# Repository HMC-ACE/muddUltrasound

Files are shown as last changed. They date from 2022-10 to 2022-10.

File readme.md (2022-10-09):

Low-Cost Underwater Ultrasonic Phased Array Research Platform
-------------------------------------------------------------

This repo contains all PCB designs, SAM4s MCU firmware, python imaging code, and documentation for the phased array research platform.

For full documentation, see [link](doc/build/html/index.html) (in a browser, you'll need to clone the repo first).

Directory
--------
 - `doc` contains the documentation source and build files (using sphinx).
 - `pcb` contains the KiCad PCB files for the channel boards and center board.
 - `mcu` contains the Atmel Studio project files for the MCU firmware.
 - `scripts` contains all python scripts to be run on the host computer.

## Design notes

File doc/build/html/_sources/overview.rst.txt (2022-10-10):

========
Overview
========

Describe assembly connection: Transducer array -> motherboard -> 9 channel boards -> i2c bus controlled by FTDI breakout -> control computer
Describe equipment connections: Hook power supplies to channel boards and motherboard by daisy chaining or w/e (star network), it will distribute power
Describe flashing boards – Atmel compiler, something something, not full depth
Describe running software on host computer – sends commands from Python over USB
Describe other subsections – one per board, maybe top level scripts

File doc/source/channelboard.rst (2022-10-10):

.. _ref-channelboard:

=============
Channel Board
=============

Outline
-------

This section contains information on the channel boards including their operation, features, configuration options, and connections. This section contains the KiCAD PCB files as well as Gerber fabrication outputs for manufacturing these boards. The Bill-of-Materials spreadsheet is also included.

File Structure
--------------

.. code:: text

  - pcb/
    - channel-board/
      - BOM.xlsx             <- Bill of Materials
      - BoatCentralboard.pro <- main KiCad 5 project file 
      - BoatCentralBoard.*   <- misc KiCad 5 project files
      - fp-lib-table         <- KiCad project footprint library location table
      - sym-lib-table        <- KiCad project symbol library location table
      - Fabrication Files/   <- GERBER files for fabrication

Board Overview
--------------

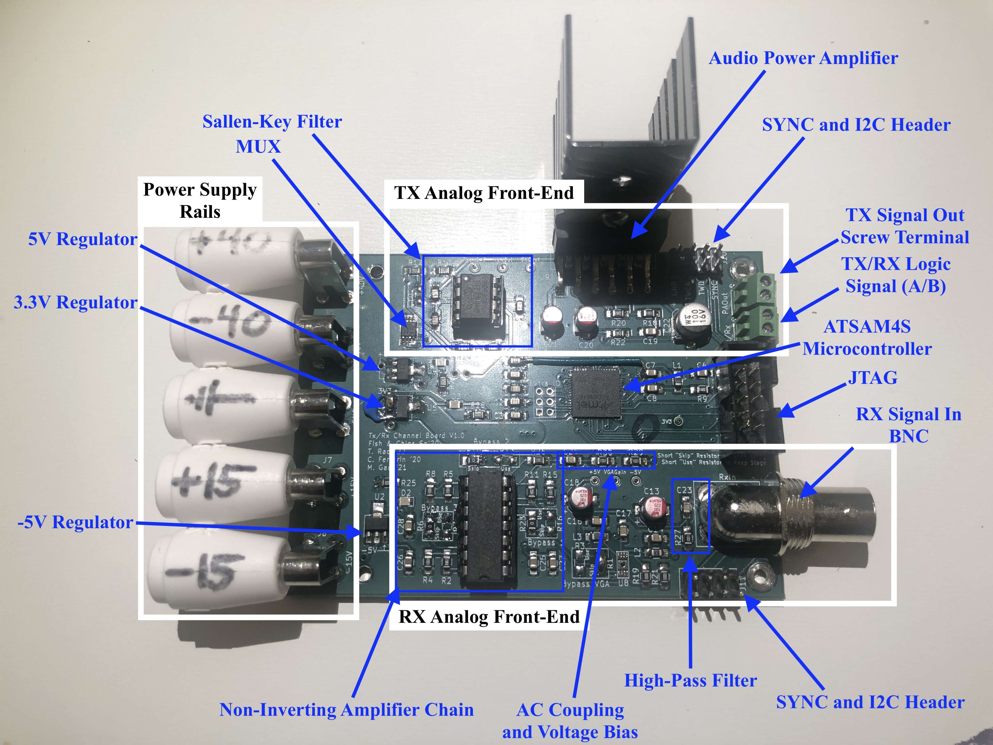
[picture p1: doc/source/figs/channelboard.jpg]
Picture of the channelboard calling out features


Each channel board is capable of driving both the transmit (TX) and receive (RX) operations for a single piezoelectric transducer in the array. An ATSAM4S microcontroller is used for PWM generation, ADC sampling, DAC output, I2C communications, and other functions. The board contains both a TX and RX analog front-end. The TX front end generates a high-voltage sinusoidal pulse to drive the transducers. This signal is output to the central motherboard with a screw terminal connector. The RX front end accepts an incoming signal from the motherboard with a BNC connector, then filters and amplifies the signal before it is sampled.  The board requires five voltage rails, typically supplied by benchtop power supplies over banana cables: ±40V, ±15V and ground. It also contains two headers at the top and bottom for the I2C and SYNC signals, so multiple channel boards can be linked on the same bus by ribbon cables. Other connectors include a JTAG programming header for the microcontroller and a screw terminal for the TX/RX switch logic signal. Due to the modular design, the entire array can be easily scaled up from the 3x3 array used in our work.

Picture of the channelboard layout for the 3x3 array

The nine-channel layout with the central board is shown in the above image. Note that not all connections between boards are shown.

Theory of Operation
-------------------

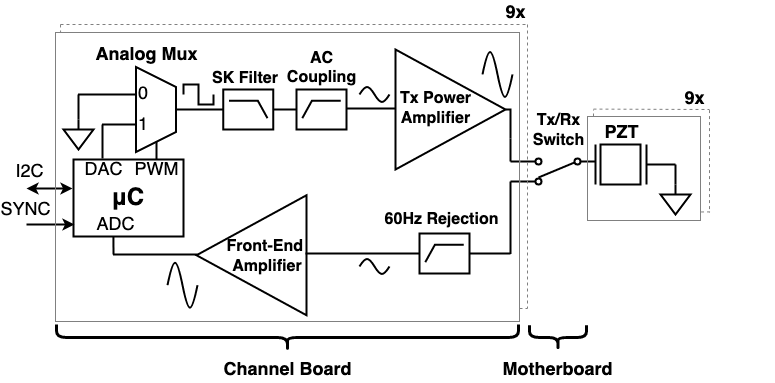
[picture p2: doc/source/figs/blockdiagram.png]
Block Diagram of the Channel Board


The channel circuitry is made of two analog front ends: a TX AFE that drives the piezoelectric transducer, and an RX AFE that amplifies and filters signals reflected back to the transducers. The image above shows a block diagram of both front-ends.

The TX AFE creates a high-voltage sinusoidal burst. The TX AFE can generate bursts with adjustable initial delays, burst amplitudes, and burst durations. When initiated by the rising edge of a digital signal called SYNC, the timer peripheral in each channel's microcontroller waits for an initial delay, then it generates a 92kHz pulse-width modulated (PWM)  signal, typically with a 100us duration. The PWM burst drives the select line of an analog multiplexer, which causes the output of the multiplexer to switch between ground and a digital-to-analog converter (DAC) voltage.  The DAC voltage is also generated by the microcontroller. The multiplexer output is driven into a set of amplifiers and filters, and because the amplifiers and filters have a fixed gain, the transmitted signal's amplitude is controlled by the DAC voltage.

One of the circuits in the TX AFE signal chain is a Sallen-Key low pass filter that is used to filter harmonics out of the multiplexer output.  Removing these harmonics converts the output from a square wave to a sine wave.  The output of the Sallen-Key filter is AC-coupled into a linear audio amplifier (the LM3886T), which amplifiers the signal to a maximum voltage swing of ±40V. The output of the amplifier is connected to a TX/RX switch (located on the central board), which in turn is connected to the piezoelectric transducers.

The RX AFE on each channel amplifies the signal with a high gain, then samples the signal coherently with the other channels. The first stage of the RX front-end is a first-order high-pass filter used for AC coupling and 60Hz rejection. The remaining stages comprise a multi-stage op-amp-based
amplifier. The final stage of the voltage amplifier drives a series current limiting resistor, AC coupling capacitor, and voltage divider used to bias the signal to a 0-3.3V range. The RX AFE output is sampled at 1 MSPS by a 12-bit ADC (with 10.5 effective bits) embedded in the channel microcontroller. Each channel's ADC used the same 1MHz clock in order to synchronize the samples. Sampling is triggered by the falling edge of the SYNC signal. Data is stored in RAM via DMA transfer and is offloaded back to the host computer for processing after sampling is complete.

Configuration Options
---------------------

The channel board offers a few options to reconfigure the TX and RX analog front-ends.

The TX Sallen-Key filter is designed to have a corner frequency near the resonant frequency of our specific transducers, which is 92kHz. The resistor and capacitor values of this filter can be changed depending on the resonant frequency of your transducers.

The RX 1st-order RC high-pass filter (R27 and C23) is tuned to reject 60Hz mains pass-through that was in our testing environment. This can be tuned to your needs, as well.

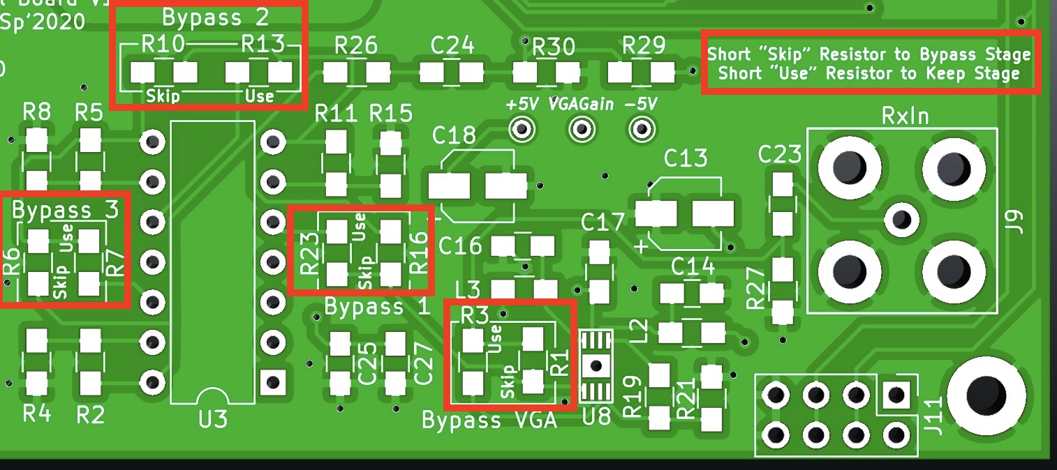
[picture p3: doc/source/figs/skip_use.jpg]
A figure showing the set of 0 ohm resistor population options


The RX amplifier chain has several 0Ω resistor population options that can change the final gain of the RX signal, as seen in the above image. There are three non-inverting amplifiers, each with a gain of approximately 20.8dB. For our tests, a gain of 41.6 dB is used (two amplifier stages are used, one is skipped).

There is a population option for an AD8337 Variable Gain Amplifier (VGA) on these boards. The gain control voltage is provided by the second DAC channel on the microcontroller. This component was not populated for our tests, and we recommend that this component not be populated if unused.

The board includes test points for the signal at each stage of the TX chain. There are also test points for all voltage rails. Indication LEDs also display whether a voltage rail is on or not.

Power Connections
-----------------

The five voltage rails — ±40V, ±15V and ground — can be supplied via banana cables from benchtop power supplies. The ±15V rail is used to generate 5V and 3.3V rails, and the -15V rail is used to generate the -5V rail on the board. The ±40V rails are used for the TX audio power amplifier.

Clock Distribution
------------------

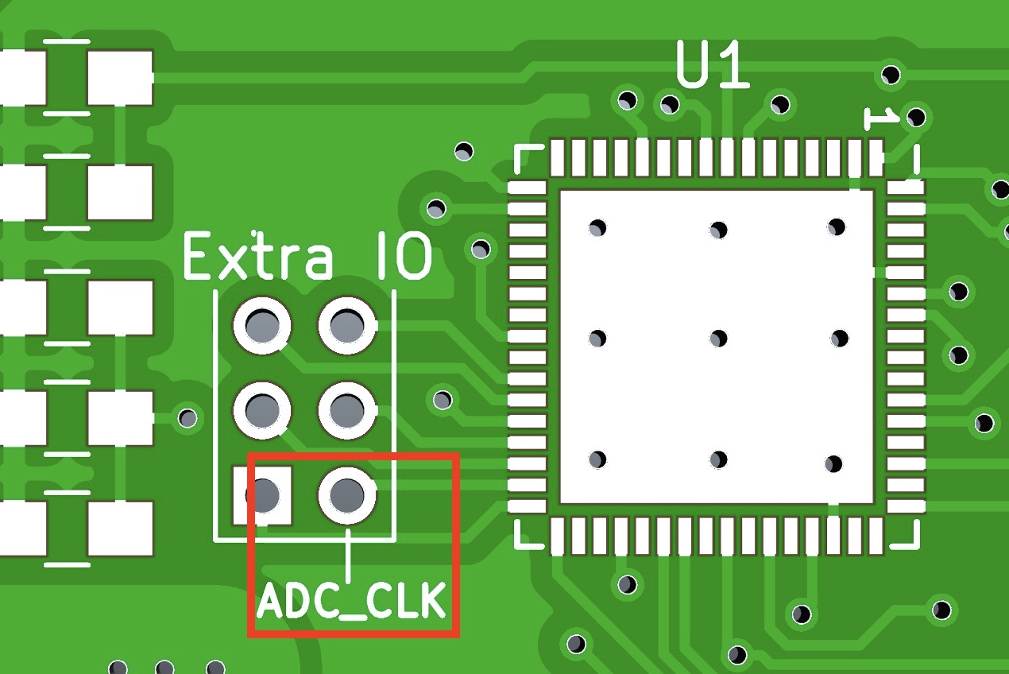
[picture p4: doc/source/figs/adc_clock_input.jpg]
Figure showing the sample clock input pin


A shared 1MHz clock must be distributed to each channel board by soldering wires to the appropriate through-hole connection on the channel board. This signal is used to generate each channel’s ADC sampling clock. The shared clock bus ensures that each channel has a synchronized sample period.

Programming Guide
-----------------

To program the channel microcontrollers the 15V rail must be provided so that the microcontrollers receive 3.3V. Plug in the JTAG connector from your programming device to the board with the correct orientation. Further instructions can be found in :ref:`ref-flashingboards`.

-- Tejus Rao

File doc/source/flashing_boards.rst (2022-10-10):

.. _ref-flashingboards:

===============
Flashing Boards
===============

The SAM4S microcontrollers onboard the channel boards were programmed using `Microchip studio`_.

Open the ``.atsln`` ("atmel solution") project file to get started. When flashing the microcontrollers, only the +15V rail needs to be powered. Open the "Programming Dialog" (`Programming Dialog Documentation`_) to flash the boards with the firmware. We use the `Jlink EDU mini`_ programmer. Go `tools > device programming` to select the options for this. Make sure that everything is wired right and connected by reading the voltage of the bus, and it should be 3.3v. Then you can try reading the device ID.

Note that you need to set the specific flavor of SAM4s MCU that you are using before you can program it, because it checks the device ID.  Our array uses the ``SAM4S4B`` and ``SAM4SA16B`` flavors, and we expect that you'll use drop-in replacements depending on part availability.

.. note::
   When programming each channel boards, the i2c address in the source code needs to be set to correspond to that of whichever board is being programmed (in line 33 of ``main.c``). A simple way to check that all boards have the correct addresses is to run ``python -i i2c_cmd.py``. If there are not 9 boards with unique addresses 1-9, the instantiation of the PhasedArray object will fail up when addressing the channel boards to write DAC values.

File Structure
--------------

.. code:: text

   - mcu/
     - rcvchain_asf_devel.atsln   <- the project file for Microchip Studio
     - rcvchain_asf_devel/
       - src/
         - main.c                 <- the main code
         - main.h                 <- the main header file
         - asf.h                  <- autogenerated include file for Atmel Software Framework
         - config/
           - config_clock.h       <- the clock configuration defines
           - config_board.h       <- unused
         - lib/
           - crc.c                <- cyclic redundancy check (crc) implementation
           - crc.h                <- crc implementation header file
        - ASF/                    <- Atmel Software Framework

Notes on the Code
-----------------

The primary purpose of the MCU firmware is to set initialize a peripherals that enable the transmit and receive functionality of each channel.
 - The I2C interface is brought up as the main method of communication with the host PC. During normal operation, when performing a write operation, the host PC either sets DAC values and transmit phase shift values. The host has other options as well, such as manually turning on and off the PWM, for debugging purposes. When performing a read operation, the host reads the channel buffer (e.g. the signal recorded by ADC). See ``TWI0_Handler`` in ``main.c`` for more information.
 - The ADC is also configured to sample from an external clock and output data to a sample buffer (``frame_buffer``) using the Peripheral DMA Controller (PDC) peripheral.
 - The PWM peripheral is set up for a 92 KHz square wave.
 - A DACC channel is used to set the amplitude of the square wave exiting from the analog multiplexer.
 - A GPIO interrupt handler ``PIOA`` is setup to start transmit on the rising edge of a sync pulse, and start receive on the falling edge.

The source code, for the most part, sticks to using the `"Advanced Software Framework"`_ (ASF), which is a Hardware Abstraction Layer (HAL) that should, theoretically, ease development. The `SAM4s datasheet`_ has good documentation of the SAM4s, and the ASF_ is documented as well. In practice, it is also helpful to use the "go to definition" feature in Microchip Studio to open the ASF file where the ASF functions are implemented.

The  ASF is bypassed in the case of the ``PIOA`` interrupt handler because the ASF-provided interrupt handler has extraneous logic that affects the execution time of the handler. The interrupt vector table (table containing all of the addresses to interrupt handlers) is replaced in order to bypass this. See comments in the ``src/main.c`` file itself for info. This file contains everything except for the clock configuration, which can be found in ``src/config/conf_clock.h``, and the crc calculation code taken from the internet (in public domain), which can be found in ``lib/crc.h``

If the user desires to expand the capabilities of the firmware, the "ASF Wizard" can be used to load the specific module for the peripheral of interest.

.. _`Microchip studio`: https://www.microchip.com/en-us/development-tools-tools-and-software/microchip-studio-for-avr-and-sam-devices#tabs
.. _`"Advanced Software Framework"`: https://asf.microchip.com/docs/latest/search.html?device=sam4s
.. _`Programming Dialog Documentation`: https://onlinedocs.microchip.com/pr/GUID-ECD8A826-B1DA-44FC-BE0B-5A53418A47BD-en-US-12/index.html?GUID-56262FE6-0BB6-49BF-974C-884E279F0A57
.. _`SAM4s datasheet`: https://ww1.microchip.com/downloads/en/DeviceDoc/Atmel-11100-32-bit%20Cortex-M4-Microcontroller-SAM4S_Datasheet.pdf
.. _ASF: https://asf.microchip.com/docs/latest/search.html?device=sam4s
.. _`Jlink EDU mini`: https://www.segger.com/products/debug-probes/j-link/models/j-link-edu-mini/

-- Alec Vercruysse

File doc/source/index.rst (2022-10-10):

.. fish-n-chips-array documentation master file, created by
   sphinx-quickstart on Tue Jul 20 15:23:22 2021.
   You can adapt this file completely to your liking, but it should at least
   contain the root `toctree` directive.

Ultrasonic Phased Array Research Platform Documentation
=======================================================

This is the main page for the documentation of the phased array research platform.

The :ref:`ref-array` page provides an overview of the assembly of the piezoelectric elements.
The :ref:`ref-motherboard` page describes the assembly and wiring of the central board.
The :ref:`ref-channelboard` page describes the assembly and wiring of the channel boards.
The :ref:`ref-flashingboards` page describes how to program the microcontrollers on each channel board.
The :ref:`ref-software` page describes how to connect to the array with the PC and run imaging scripts. It also includes the :ref:`ref-api`.

.. toctree::
   :maxdepth: 2
   :caption: Contents:

   transducer
   motherboard
   channelboard
   flashing_boards
   running_software
   usage

Indices and tables
==================

* :ref:`genindex`
* :ref:`modindex`
* :ref:`search`

Building this Documentation
---------------------------

This documentation is built with sphinx. To rebuild the documentation, first ensure that you have a virtual environment with all the required modules for the python scripts. The virtual environment also needs ``sphinx`` and ``sphinx_rtd_theme``. In a terminal with the ``doc`` folder as the working directory, run ``make clean; make html`` to build. All files should appear in ``doc/build``.

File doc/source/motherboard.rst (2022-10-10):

.. _ref-motherboard:

===========
Motherboard
===========

This section contains information about the central board, or motherboard, used to route TX signals to and RX signals from the transducer array. This section contains the KiCAD PCB files as well as Gerber fabrication outputs for manufacturing these boards. The Bill-of-Materials spreadsheet is also included.

File Structure
--------------

.. code:: text

  - pcb/
    - center-board/
      - BOM.xlsx             <- Bill of Materials
      - BoatCentralboard.pro <- main KiCad 5 project file 
      - BoatCentralBoard.*   <- misc KiCad 5 project files
      - fp-lib-table         <- KiCad project footprint library location table
      - sym-lib-table        <- KiCad project symbol library location table
      - Fabrication Files/   <- GERBER files for fabrication

Board Overview
--------------

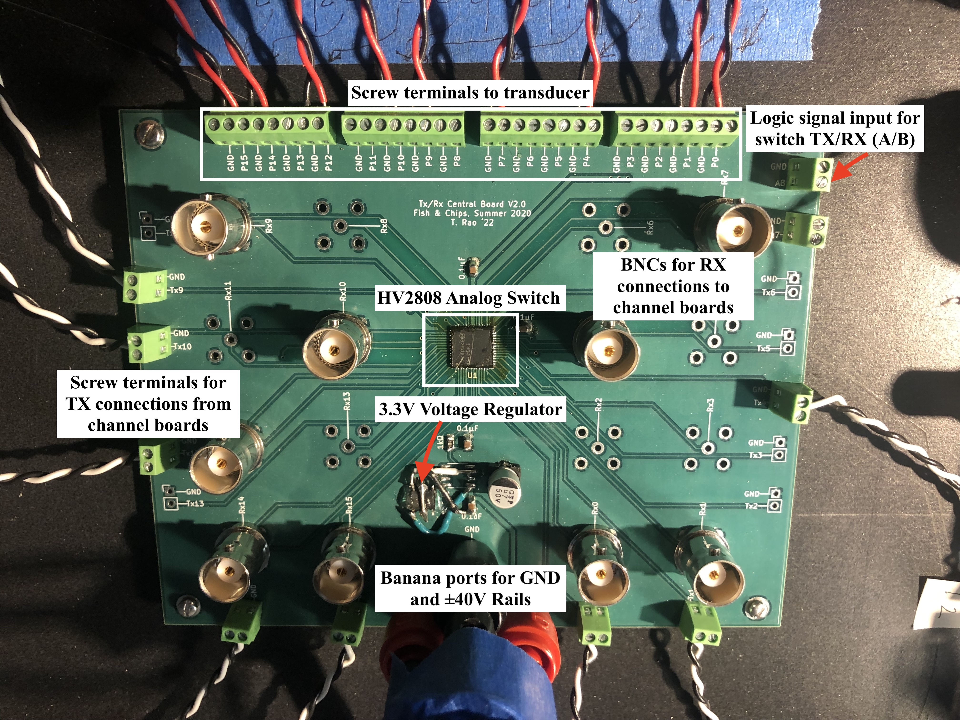
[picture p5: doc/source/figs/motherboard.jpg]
Picture of the motherboard calling out features


  Picture of the Motherboard
          
The central board hosts a Microchip HV2808 32-channel high-voltage analog switch. This device acts as a TX / RX switch to isolate the TX and RX analog front ends during their respective operations. This board breaks out the HV2808 into 32 ports, enabling a 16 channel TX / RX switch. The other components on this board are a 3.3V voltage regulator and power supply decoupling.

.. note::
   Note that the board pictured does not have all components soldered. Only connections for channels 0 through 8 were populated since this was used for a 9 channel (3x3) transducer array.

.. note::
   Note that the rework visible on the board pictured was due to an incorrect voltage regulator footprint, which has since been updated in the PCB files.

Connections
-----------

The RX connections use vertical-launch female BNC ports to improve signal integrity, while the TX connections use side-launch screw terminals. Connections between the TX screw terminals on the channel boards and this central board were made with twisted pairs of 22 AWG solid-core wire. Other connectors include the screw terminal bank for connecting to the piezoelectric transducer array and banana ports for positive and negative 40V rails, and ground. The ±40V and ground rails should be linked to the same power rails as the channel board. Additionally, the screw terminal labeled “A/B” is the logic input for switching the HV2808 conduction path. It’s compatible with a 3.3V signal from the channel microcontrollers.

All channel boards contain connections to output the A/B switching signal to the central board, but only one must be connected. This is nominally channel 0. Connection between the channel 0 board and central board A/B terminal is done over a twisted pair of 22 AWG solid-core wire.

Soldering Instructions
----------------------

If using solder paste with or without a stencil, we recommend soldering the surface-mount components before the larger through-hole connectors. Ensure connections on the QFN-package HV2808 are not shorted. Perform rework as necessary before proceeding to soldering the through-hole components.

-- Tejus Rao

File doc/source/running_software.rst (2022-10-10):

================
Running Software
================

We communicate with the nine channel boards with a host PC and a FTDI FT2232H-56Q evaluation board, which contains an FTDI FT2232H USB to I2C device. All python software is written to run on the host PC.

This API documentation provides the docstrings for the methods used to interact with the Phased Array through the FT2232H chip. All PC to board and board to PC communication is done with methods in the `i2c_cmd` module. Also documented here is `das_scan`, which is the module that contains all of the different imaging scripts, and `visualize`, which is the module that allows "replay" of the imaging done in `das_scan`.

All of these modules are located in the ``scripts/`` directory, and can be run themselves (not just imported).

.. _ref-software:

Communicating with the Array
----------------------------

Wiring
~~~~~~

See below for i2c wiring (also documented in pyftdi_)

.. _pyftdi: https://eblot.github.io/pyftdi/api/i2c.html#wiring
.. _`pyftdi documentation`: https://eblot.github.io/pyftdi/api/i2c.html#open-collector-bus 

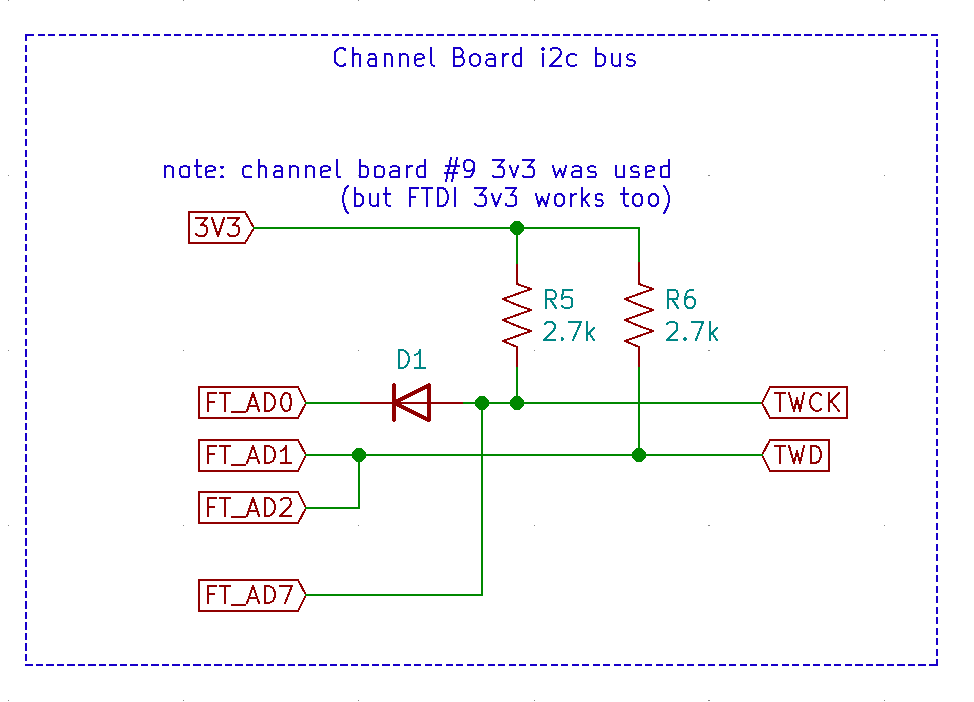
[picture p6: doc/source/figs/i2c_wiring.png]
I2C wiring


  Fig.1: FT2232H i2c wiring. note the `FT_` prefix won't appear on the silkscreen of the `FT2232H-56Q` itself.

The SYNC pulse is also generated by the GPIO of the `FT2232H`, and is used by all boards to start a TX operation at the exact same time, and an RX operation at the exact same time. This extremely important to the operation of the phased array since any time difference between the start of the TX or RX operations for different boards will cause destructive phase differences during beamforming. The internal oscillators in the microcontrollers have some frequency offset relative to each other, so the FT2232H provides a SYNC pulse to trigger both the start of the TX and start of the RX operations. The rising edge of the SYNC pulse controls the start of the TX operation, and the falling edge controls the start of the RX operation. We need to have a deterministic and precise amount of time between the start of a TX and the start of an RX, since this delay has to be taken into account when range-finding. Furthermore, we want to be able vary the amount of time between the start of a TX and the start of an RX sequence, since having some delay between the end of the TX and the start of the RX allows the piezos to stop "ringing" before receiving the echo signals. This affects the minimum range that the phased array can image. The FT2232H cannot provide the deterministic timing for the SYNC pulse because it is controlled via USB by a non real time operating system (e.g. the host computer), so the pulse width is non-deterministic. We solve this by using a 555 timer in a `monostable configuration`_, with a trim potentiometer to allow us to vary the pulse width. The 555 timer is triggered by a GPIO output of the FT2232H. In our implementation, the 556 timer was tuned to a 800 us delay. If this is changed, ``PhasedArray.delay`` should be set to what it is tuned to in ``i2c_cmd.py``.

.. _`monostable configuration`: https://www.electronics-tutorials.ws/waveforms/555_timer.html

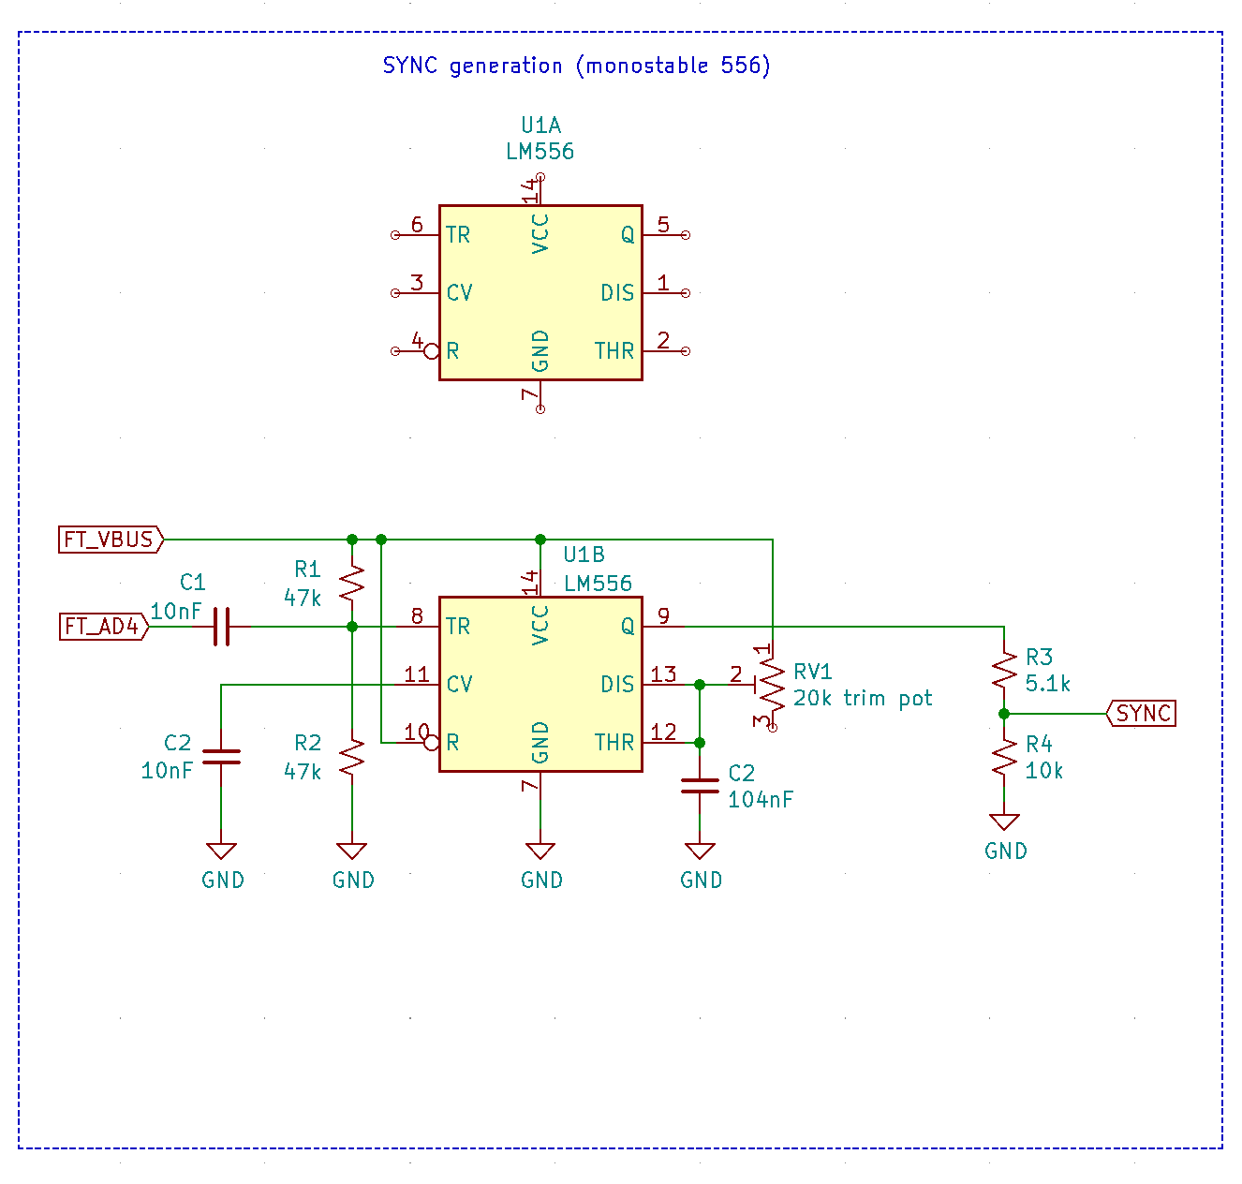
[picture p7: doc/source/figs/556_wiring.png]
555/556 wiring for SYNC pulse generation.


  Fig.2: 555/556 wiring for SYNC pulse generation.

The wiring schematic file can be found in ``./figs/fish-n-chips-ft2232h``.

Software Setup
~~~~~~~~~~~~~~

To run the python code, first set up a virtual environment using the provided ``requirements.txt``. Note that ``pyfti`` is used to interface with the FTDI FT2232H-56Q evaluation board.

Ensure the FTDI chip is connected via USB to the host PC. Running ``python -i i2c_cmd.py`` will start python in interactive mode, and `i2c_cmd` will create a `PhasedArray` and `ChannelBoard` object for the user to interact with. Running this is the simplest way to check that the host PC is able to communicate with each channel board.

Once the `ChannelBoard` object is instantiated, `i2c_cmd` facilitates simple analog front-end (AFE) debugging. For example, ``ChannelBoard.write(BoardApi.START_PWM)`` will indefinitely turn on the PWM for the instantiated channel board. In the REPL, see ``help(PhasedArray)``, ``help(ChannelBoard)``, and ``help(BoardAPI)`` for more options.

To facilitate debugging the receive analog front end, `read_frambuffer.py` enables simple visualization of samples recorded by the ADC of a channel board. Run ``python3 read_framebuffer.py -h`` for usage information.

.. note:: The i2c read/writes fail occasionally, and we make sure to allow for many re-tries when things go wrong, as well as check the integrity of read data with a crc32 checksum. If an i2c or checksum error occurs, it usually resolves within 10 tries, but very rarely takes longer.

.. _ref-imaging:

Imaging
-------

All the code for the different types of swept-beam imaging is housed in ``das_scan.py``. Note that each type of imaging takes a very long time -- points are scanned in a 2D or 3D space by sending a steered transmit pulse and performing beamforming on the receive. The time taken to perform each set of transmit/receive is limited mostly by the slow speed of the i2c communication.

Running `das_scan.py` as main will run a spherical imaging script. Note that there will be a prompt for the "setup:", which is simply a note the user can write in order to name or comment on the specific image run being taken, for when the captured data is later analyzed.

Logging is enabled by default into a directory called `data/` (relative to the `scripts/` directory). Running `visualize.py`  allows the user to interactively select and view an imaging run to inspect and review.

To run a 2D scan, try running the ``scan_x_slice`` function that `das_scan` provides. There is no raw data logging option for this yet.

File Structure
--------------

.. code:: text

          - scripts/
            - das_scan.py         <- The top-level code for swept-beam imaging.
            - i2c_cmd.py          <- The code containing the interface to each channel board.
            - image.py            <- The code to perform delay-sum beamforming.
            - phaseshifts.py      <- The code to calculate phase shifts for steering directions.
            - read_framebuffer.py <- Debug code to visualize the output of an ADC capture.
            - requirements.txt    <- Used to set up a virtual environment with the necessary python packages.
            - visualize.py        <- Used to visualize (e.g. replay) logged data from das_scan.

.. _ref-api:
              
API Documentation
-----------------

.. toctree::
   :maxdepth: 2
   :caption: Contents:

   api/i2c_cmd
   api/das_scan
   api/visualize

-- Alec Vercruysse

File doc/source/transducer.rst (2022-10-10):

.. _ref-array:

================
Transducer Array
================

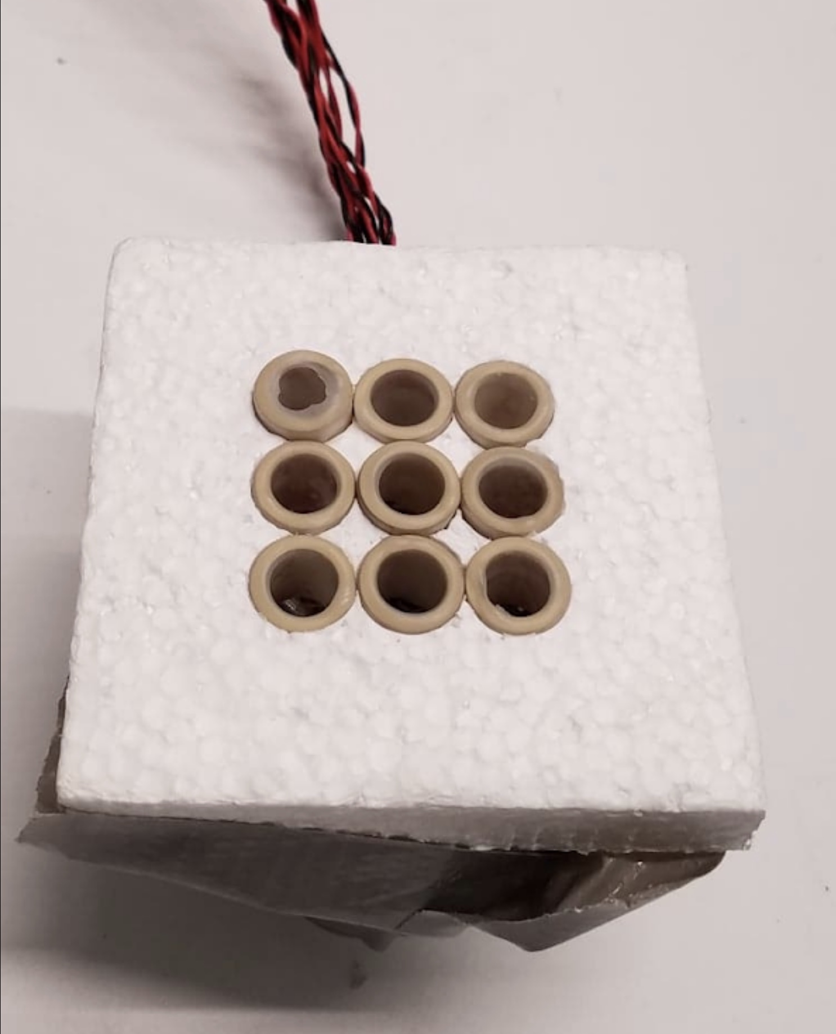
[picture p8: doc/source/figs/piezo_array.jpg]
Image of pzt array.


Outline
-------

This section contains information on the piezoelectric transducer array, the process for coating each transducer with silicone, and guidelines for creating the array assembly. The transducers used are the `American Piezo (APC) 42-1012`_ (may be available as the 42-1011, as well) cylindrical tube.

Soldering to the transducers
----------------------------

The piezoelectric cylinders are plated with a very delicate layer of metal, which enables us to solder connections to them. Take care to follow the instructions outlined by American Piezo when soldering connections to them. We recommend purchasing the American Piezo `soldering kit`_ to practice soldering to piezo samples. It’s critical to use low-temperature solder and flux, and to minimize the duration of direct heat in contact with the transducers in order to preserve the metal plating on the transducer and prevent the ceramic from cracking.

The outer ring of the cylinder is considered to be ground.

The procedure that we used is outlined here:

*Materials (per transducer)*
 - APC 42-1012 piezo
 - 5ft of 22 AWG solid-core wire (twisted pairs, usually red and black or white and black)
 - Flux paste
 - Low-temperature rosin-core solder
 - Soldering iron
 - Flux remover spray or IPA
 - Kapton or masking tape

*Instructions*
 1. Secure the piezo cylinder with tape to your work surface
 2. Strip about 5mm of insulation off both ends of the wires
 3. Apply a layer of solder to the exposed wires (aka tinning)
 4. Coat the exposed wire with flux paste. Rosin flux paste will also help the wire adhere to the surface of the piezo before soldering since it is slightly sticky.
 5. Mount or hold your wires to the transducer with the ground wire on the outer surface and the signal wire on the inner surface of the cylinder.
 6. Melt a bead of solder onto the soldering iron tip
 7. Carefully press the melted solder on the tip to the exposed wires on the piezo ring. When the solder has flowed and created a connection, remove the iron. The joint should be flat and shiny.
 8. Remove excess flux
 
Coating Process
---------------

The ceramic transducers have an acoustic impedance that is quite different from that of water. We coat the transducers with a thin layer of silicone, which has an acoustic impedance much closer to that of water, to increase our power transfer into the water. The coating we used is the `Silicone Solutions SS-6B`_.

This process should be completed after soldering wires to the piezos. Note that the process can be messy, so prepare a surface for the excess silicone to drip onto beforehand. We recommend hanging the transducers by their wires over an open area with tape and using paper towels to protect the surface below. We space the transducers a couple inches apart.

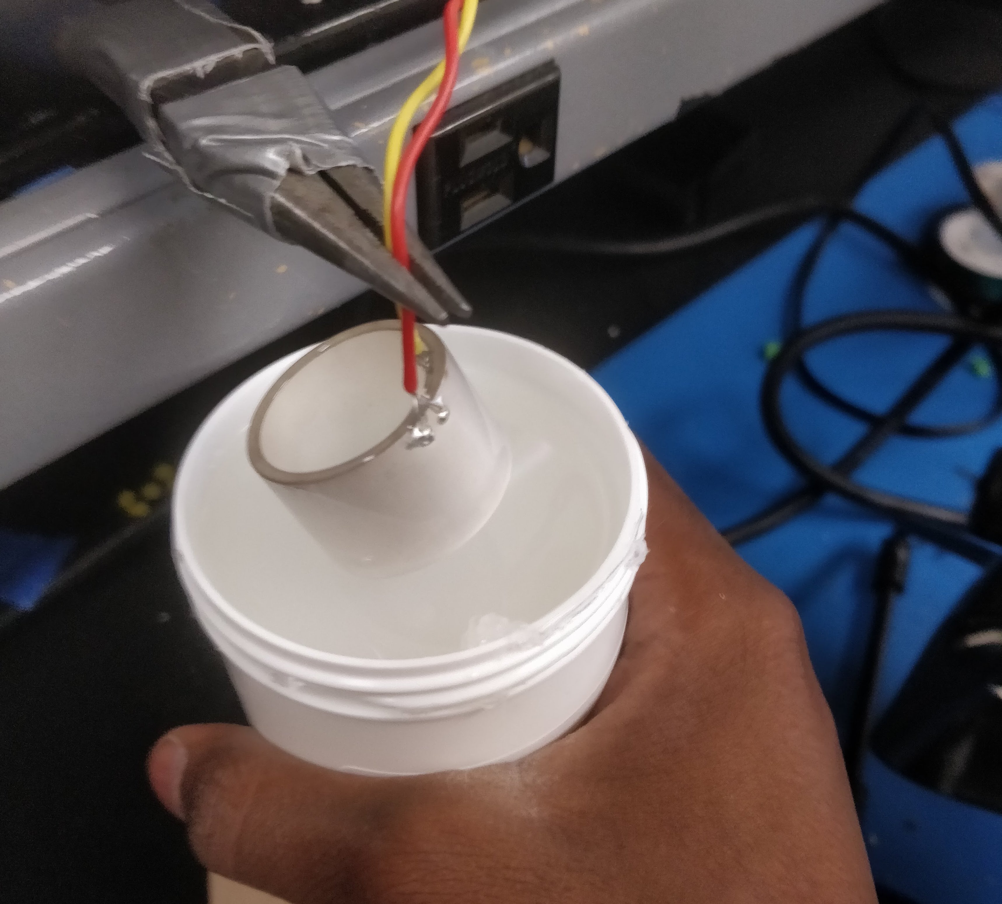
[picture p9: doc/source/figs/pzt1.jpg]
Inserting the tub of coating around the pzt.


Without moving the piezo, insert the tub of coating around each. Ensure that the entire piezo is coated, along with any exposed wire.

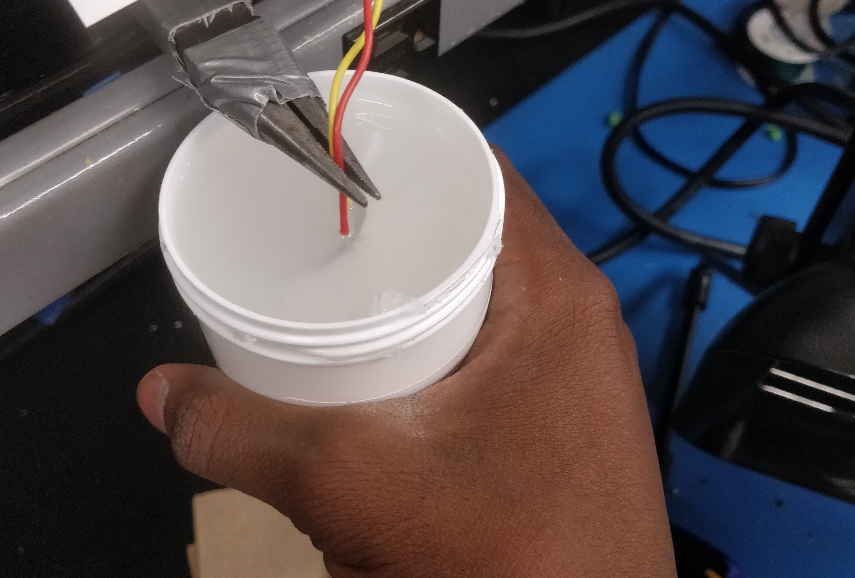
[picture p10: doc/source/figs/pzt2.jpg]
Second image, inserting the tub of coating around the pzt.


Slowly remove the tub from the cylinder and repeat on every piezo. Let the coating dry in a well-ventilated area for the manufacturer’s recommended cure time.

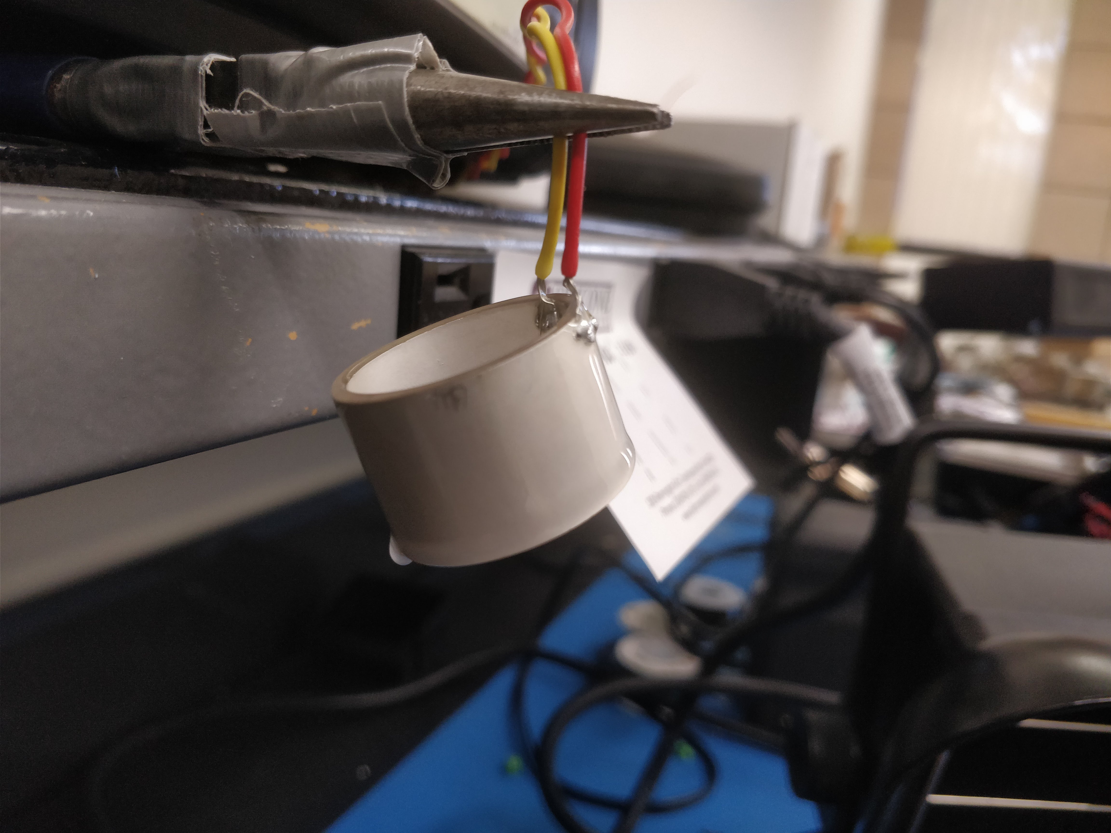
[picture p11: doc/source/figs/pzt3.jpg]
Drying coated pzt.


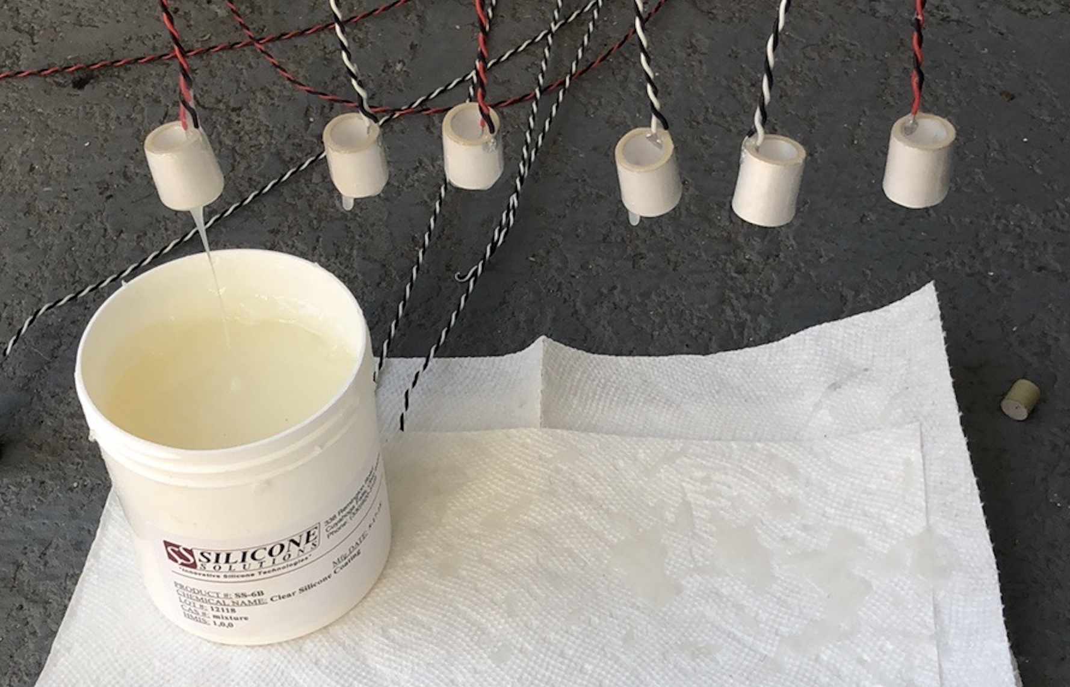
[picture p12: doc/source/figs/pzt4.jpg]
rack of drying coated pzts.


Assembly
--------

Our array is encased in a polystyrene shell. This ensures consistent spacing. We use a 1/8” acrylic piece as a backplate for the array, with holes drilled for the transducer wires to pass through. We mount this assembly on a PVC pipe and use zip-ties for strain relief on the transducer wires.

.. _`American Piezo (APC) 42-1012`: https://www.americanpiezo.com/standard-products/piezo-tubes.html
.. _`soldering kit`: https://www.americanpiezo.com/standard-products/solder-kit.html
.. _`Silicone Solutions SS-6B`: https://siliconesolutions.com/conformal-coatings/ss-6bclear.html

-- Tejus Rao

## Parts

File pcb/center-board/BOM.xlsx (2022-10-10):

Component | Reference | Vendor | Vendor Part Number | Quantity Per Board | Cost for 1 | Cost for Board
Tx/Rx Switch | U1 | Microchip | HV2808K6-G | 1 | $17.53 | $17.53
3.3V Regulator | U2 | Digi-Key | LM2936HVBMAX3.3/NOPBCT-ND | 1 | $1.93 | $1.93
0.1uF SMD Capacitor | C2, C3, C4, C5, C6 | Digi-Key | 311-2083-1-ND | 6 | $0.20 | $1.20
1uF SMD Capacitor | C1 | Digi-Key | GRJ21BC72A105KE11L | 2 | $0.51 | $1.02
47uF SMD Electrolytic Capacitor | C7 | Digi-Key | 493-2225-1-ND | 1 | $0.50 | $0.50
1kΩ SMD Resistor | R1 | Digi-Key | 311-1.00KCRCT-ND | 1 | $0.01 | $0.01
±40V Banana Jack (Red) | J33, J34 | Digi-Key | CT3151V1-2-ND | 2 | $2.05 | $4.10
GND Banana Jack (Black) | J35 | Digi-Key | CT3151V1-0-ND | 1 | $2.05 | $2.05
Vertical BNC Connector | J2, J4, J6, J8, J10, J12, J14, J16, J18, J20, J22, J24, J26, J28, J30, J32 | Digi-Key | ACX1051-ND | 16 | $2.83 | $45.28
Screw Terminal Block, 2-Pin | J1, J3, J5, J7, J9, J11, J13, J15, J17, J19, J21, J23, J25, J27, J29, J31 | Pololu | 2491 | 17 | $2.02 | $34.34
Screw Terminal Block, 8-Pin | J36, J37, J38, J39 | Polou | 2497 | 4 | $2.02 | $8.08
 |  |  |  |  |  | $116.04

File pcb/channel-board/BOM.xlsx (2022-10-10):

Category | Component | Reference | Value | Package | Vendor | Vendor Part Number | Quantity Per Board | Cost for 1 Part | Total Cost per Board | Vendor Description
ICs | ATSAM4S4B MCU | U1 |  | QFN-64, 9x9mm, 0.5mm Pitch | Digi-Key | ATSAM4S4BA-MU-ND | 1 | $3.82 | $3.82 | IC MCU 32BIT 256KB FLASH 64QFN
 | -5V Voltage Regulator | U2 |  | SOT-89-3 | Digi-Key | MC79L05F-TPMSCT-ND | 1 | $0.38 | $0.38 | IC REG LINEAR -5V 100MA SOT89
 | TL084CP Quad Op Amp | U3 |  | DIP-14 | Digi-Key | 296-12951-5-ND | 1 | $1.52 | $1.52 | Operational Amplifiers - Op Amps Quad JFET Neg Input
 | +5V Voltage Regulator | U4 |  | SOT-89-3 | Digi-Key | ZXTR2005Z-13DICT-ND | 1 | $0.53 | $0.53 | IC REG LINEAR 5V 38MA SOT89
 | 3.3V Voltage Regulator | U5 |  | SOT-89-3 | Digi-Key | AZ1117CR-3.3TRG1DICT-ND | 1 | $0.38 | $0.38 | IC REG LINEAR 3.3V 600MA SOT89-3
 | MAX4644 MUX | U6 |  | MSOP-8, 3x3mm, 0.65mm Pitch | Digi-Key | MAX4644EUA+-ND | 1 | $2.15 | $2.15 | IC SWITCH SPDT 8UMAX
 | MCP601 Op Amp | U7 |  | DIP-8 | Digi-Key | MCP601-E/P-ND | 1 | $0.48 | $0.48 | IC OPAMP GP 1 CIRCUIT 8DIP
 | AD8337 VGA | U8 |  | LFCSP-8, 3x3mm, 0.5mm Pitch | Digi-Key | AD8337BCPZ-REEL7CT-ND | 1 | $6.19 | $6.19 | IC VGAIN AMP 8LFCSP
 | LM3886T Power Amplifier | U9 |  | TO-220-11 | Digi-Key | LM3886T/NOPB-ND | 1 | $6.82 | $6.82 | IC AMP CLSS AB MONO 68W TO220-11
Power Indication | 300Ω SMD Resistor | R24, R25 | 300Ω | Hand Solder 0805 | Digi-Key | 311-300CRCT-ND | 2 | $0.10 | $0.20 | RES SMD 300 OHM 1% 1/8W 0805
 | 120Ω SMD Resistor | R28 | 120Ω | Hand Solder 0805 | Digi-Key | 311-120CRCT-ND | 1 | $0.10 | $0.10 | RES SMD 120 OHM 1% 1/8W 0805
 | Green SMD LED | D1, D2, D3 |  | Hand Solder 0805 | Digi-Key | 296-12951-5-ND | 3 | $0.59 | $1.77 | Standard LEDs - SMD AlInGaP Green
Power Sequencing | 10nF SMD Capacitor | C1, C23 | 10nF | Hand Solder 0805 | Digi-Key | 311-1475-1-ND | 2 | $0.12 | $0.24 | 10000pF ±10% 100V Ceramic Capacitor X7R 0805 (2012 Metric)
 | 4.7uF SMD Capacitor | C4 | 4.7uF | Hand Solder 0805 | Digi-Key | 490-12753-1-ND | 1 | $0.25 | $0.25 | 4.7µF ±10% 25V Ceramic Capacitor X5R 0805 (2012 Metric)
 | 2.2uF SMD Capacitor | C5 | 2.2uF | Hand Solder 0805 | Digi-Key | 490-14467-1-ND | 1 | $0.22 | $0.22 | 2.2µF ±10% 25V Ceramic Capacitor X7R 0805 (2012 Metric)
 | 10uH SMD Inductor | L1 | 10uH | Hand Solder 0805 | Digi-Key | 445-8656-1-ND | 1 | $0.16 | $0.16 | 10µH Shielded Multilayer Inductor 300mA 680mOhm 0805 (2012 Metric)
 | 1Ω SMD Resistor | R9 | 1Ω | Hand Solder 0805 | Digi-Key | 311-1.00CRCT-ND | 1 | $0.10 | $0.10 | RES SMD 1 OHM 1% 1/8W 0805
Connectors | Screw Terminal 1x2 | J1, J6 |  | Screw Terminal Block 2-Pin | Digi-Key | A98333-ND | 1 | $0.92 | $0.92 | 2 Position Wire to Board Terminal Block Horizontal with Board 0.100" (2.54mm) Through Hole
 | JTAG-10 Pin | J2 |  | Pin header 2x5 1.27mm | Digi-Key | 612-FTSH-105-01-F-D-K-ND | 1 | $3.99 | $3.99 | CONN HEADER VERT 10POS 1.27MM
 | Power Banana Jacks | J3, J4, J5, J7, J8 | ±40, ±15 | 4-Pin Banana Jack Red | Digi-Key | BKCT3151SP-2-ND | 5 | $2.05 | $10.25 | CONN BANANA JACK SOLDER RED
 | Rx In BNC Connector | J9 |  | Right-Angle Coaxial Connector | Digi-Key | A97570-ND | 1 | $2.91 | $2.91 | CONN BNC JACK R/A 50 OHM PCB
 | DIP-14 Socket | U3 |  | DIP-14 | Digi-Key | AE9989-ND | 1 | $0.22 | $0.22 | CONN IC DIP SOCKET 14POS TIN
 | DIP-8 Socket | U7 |  | DIP-8 | Digi-Key | AE9986-ND | 1 | $0.18 | $0.18 | CONN IC DIP SOCKET 8POS TIN
 | Pin Headers, 2x4 for Ribbon | J10, J11 |  | Pin Headers 2x40, 2.54mm Pitch | Digi-Key | 609-3203-ND | 2 | $0.47 | $0.94 | CONN HEADER R/A 40POS 2.54MM
Tx/Rx Amplifiers | 0Ω SMD Resistor | R1, R3, R6, R7, R10, R13, R16, R23 | 0Ω | Hand Solder 0805 | Digi-Key | 311-0.0ARCT-ND | 8 | $0.10 | $0.80 | RES SMD 0 OHM JUMPER 1/8W 0805
 | 20kΩ SMD Resistor | R12, R20 | 20kΩ | Hand Solder 0805 | Digi-Key | 311-20.0KCRCT-ND | 2 | $0.10 | $0.20 | RES SMD 20K OHM 1% 1/8W 0805
 | 6.98kΩ SMD Resistor | R14 | 6.98kΩ | Hand Solder 0805 | Digi-Key | 311-6.98KCRCT-ND | 1 | $0.10 | $0.10 | RES SMD 6.98K OHM 1% 1/8W 0805
 | 10kΩ SMD Resistor | R2, R5, R11, R17 | 10kΩ | Hand Solder 0805 | Digi-Key | 311-10.0KCRCT-ND | 4 | $0.10 | $0.40 | RES SMD 10K OHM 1% 1/8W 0805
 | 1kΩ SMD Resistor | R4, R8, R15, R18, R26, R27, R29, R30 | 1kΩ | Hand Solder 0805 | Digi-Key | 311-1.00KCRCT-ND | 8 | $0.10 | $0.80 | RES SMD 1K OHM 1% 1/8W 0805
 | 100Ω SMD Resistor | R19, R21 | 100Ω | Hand Solder 0805 | Digi-Key | 311-100CRCT-ND | 2 | $0.10 | $0.20 | RES SMD 100 OHM 1% 1/8W 0805
 | 15kΩ SMD Resistor | R22 | 15kΩ | Hand Solder 0805 | Digi-Key | 311-15.0KCRCT-ND | 1 | $0.10 | $0.10 | RES SMD 15K OHM 1% 1/8W 0805
 | 10pf SMD Capacitor | C9 | 10pF | Hand Solder 0805 | Digi-Key | 311-1834-1-ND | 1 | $0.15 | $0.15 | CAP CER 10PF 100V C0G/NPO 0805
 | 2.2nF SMD Capacitor | C11 | 2.2nF | Hand Solder 0805 | Digi-Key | 311-1479-1-ND | 1 | $0.12 | $0.12 | CAP CER 2200PF 100V X7R 0805
 | 0.1uF SMD Capacitor | C2, C3, C6, C7, C8, C12, C14, C16, C20, C21, C24, C25, C26, C27, C28, C30, C32 | 0.1uF | Hand Solder 0805 | Digi-Key | 311-2083-1-ND | 17 | $0.20 | $3.40 | CAP CER 0.1UF 100V X7R 0805
 | 0.1uF SMD Electrolytic Cap | C20, C21 | 0.1uF | 4x5.7 electrolytic shell | Digi-Key | 732-8266-1-ND | 2 | $0.17 | $0.34 | 0.1µF 50V Aluminum Electrolytic Capacitors Radial, Can - SMD 5000 Hrs @ 105°C
 | 10uF SMD Electrolytic Cap | C13, C18 | 10uF | 4x5.7 electrolytic shell | Digi-Key | 732-8503-1-ND | 2 | $0.19 | $0.38 | 10µF 35V Aluminum Electrolytic Capacitors Radial, Can - SMD 2000 Hrs @ 105°C
 | 10uF SMD Capacitor | C29 | 10uF | Hand Solder 0805 | Digi-Key | 399-C0805C106K8PAC7210CT-ND | 1 | $0.14 | $0.14 | CAP CER 10UF 10V X5R 0805
 | 1uF SMD Capacitor | C10, C33 | 1uF | Hand Solder 0805 | Digi-Key | 399-C0805C105J3REC7800CT-ND | 2 | $0.13 | $0.26 | CAP CER 0805 1UF 25V X7R 5%
 | 910pF SMD Capacitor | C15 | 910pF | Hand Solder 0805 | Digi-Key | 478-12759-1-ND | 1 | $0.29 | $0.29 | CAP CER 910PF 100V X7R 0805
 | 1nF SMD Capacitor | C17 | 1nF | Hand Solder 0805 | Digi-Key | 311-1472-1-ND | 1 | $0.13 | $0.13 | CAP CER 1000PF 100V X7R 0805
 | 22uF SMD Capacitor | C19, C31 | 22uF | Hand Solder 0805 | Digi-Key | 490-9951-1-ND | 2 | $0.46 | $0.92 | CAP CER 22UF 10V X5R 0805
 | 100uF SMD Electrolytic Cap | C22 | 100uF | 6.3x5.7 electrolytic shell | Digi-Key | 493-2105-1-ND | 1 | $0.30 | $0.30 | CAP ALUM 100UF 20% 16V SMD
 | 120nH SMD Inductor | L2, L3 | 120nH | Hand Solder 0805 | Digi-Key | 445-8984-1-ND | 2 | $0.18 | $0.36 | 120nH Shielded Multilayer Inductor 300mA 200mOhm Max 0805 (2012 Metric)
Equipment | Heat Sink | N/A |  | TO-220 | Digi-Key | 590302B03600G-ND | 1 | $1.03 | $1.03

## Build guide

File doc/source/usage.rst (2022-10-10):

=====
Usage
=====

1. Follow the instructions in :ref:`ref-array` to assemble the pzt array.
2. Follow the instructions in :ref:`ref-channelboard` to hook up all power supplies and clock distribution, and ensure there are no shorts between any of the power rails. Flash the boards with the MCU firmware using the directions in :ref:`ref-flashingboards`
3. Follow the instructions in :ref:`ref-motherboard` to hook up each channel board to the motherboard, and the motherboard to the Piezo array.
4. Wire the ft2232h-56q board and 556 timer for i2c communication and sync pulse generation, respectively, as per the directions in :ref:`ref-software`.
5. Follow the instructions in :ref:`ref-software` to establish a connection with the boards.
6. Follow the instructions in :ref:`ref-imaging` to run an imaging script. See the :ref:`ref-api` for more detailed software usage.

.. warning:: The imaging speed is severely limited by the transfer times on the i2c bus. A single transmit/receive takes a few seconds, but a 3D scan takes on the order of an hour, since the beam is swept.

-- Alec Vercruysse

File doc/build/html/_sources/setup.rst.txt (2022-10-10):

Setup
=====

Hardware
~~~~~~~~

PSUs
----

The Phased Array requires a lot of different power channels, and, in the absence of a dedicated PSU board (which is on the list of things to do!), requires a complicated PSU setup.

The main issue is that to generate all the voltage, isolated power supplies need to be used, and only at one point should ground be referenced to earth ground. This helps avoid ground loops. In general, the principle of "star grounding" should be followed as much as possible to avoid signal integrity issues (although we have issues with this, like the ground connections on our i2c/sync bus).

In the past, +/- 40V was generated with two `VOLTEQ HY5005D` power supplies. The positive of one was linked to the negative of the other, with that point being the ground reference, in order to generate both a positive and negative voltage. Each PSU should draw approximately .5A when all power amps on the channel boards are powered. Note that these rails only power those power amps and central tx/rx switch, so those PSUs don't need to be on when debugging the MCUs or the receive chain! Furthermore, The power amps we use right now have their heatsinks at -40V, so be careful touching anything (such as probe ground leads, which are earth referenced) to them when these PSUs are on!!

The 15V rail was generated with a `CircuitSpecialists.com CSI5003X5` PSU. This was set to only 9V, since the 15V rail just gets regulated down to 3v3 (for the MCU) and 5v (for the opamps), and setting it to 9V lets the hydrophone preamp get powered off of it, if necessary. This should draw a little over an amp with everything on, so the `Agilent E3630A` PSUs that are usually in the tank room *won't* work for this!

The -15V rail was generated with an incredibly massive and sketchy PSU (it was unregulated, so it's voltage was a function of current draw). I would recommend looking for another PSU, but again it needs to handle more than .5A of power (the Agilent PSU didn't work). This rail powers just the opamps in the tx and rx chain.

The ft2232h chip and the 556 timer are driven from the USB bus. Note that when everything is powered, The chip will still have power via USB, which it might try to use to "back power" some of the MCUs via the i2c rail. A similar situation happens with the jlink chip. Disconnect these when turning power off to the array.

Make sure to use a multimeter to check that there is no continuity between any of the rails before powering everything on!

ft2232h
-------
This chip is now what we use to connect to the computers via the i2c connection. We switched in spring 2021 since the buspirate was very slow, especially when reading the large amounts of data during an rx sequence. We used the `ft2232h-56Q` evaluation board the whole time so that we did not have to deal with rolling our own board. Note, however, that this solution is still suboptimal, since the FT2232H cannot tri-state the buffer (see `pyftdi documentation`_). Furthermore, i2c over such long distances with so many devices isn't great for neither EMI nor rise-times (due to bus capacitance). It is generally a pretty slow communications protocol, so in the future, we are trying to switch.

The i2c read/writes fail occasionally, and we make sure to allow for many re-tries when things go wrong, as well as check the integrity of read data with a crc32 checksum. If an i2c or checksum error occurs, it usually resolves within 10 tries, but very rarely takes longer. It has never taken 50!

See below for i2c wiring (also documented in pyftdi_)

.. _pyftdi: https://eblot.github.io/pyftdi/api/i2c.html#wiring
.. _`pyftdi documentation`: https://eblot.github.io/pyftdi/api/i2c.html#open-collector-bus 

.. figure:: figs/i2c_wiring.png
  :width: 400
  :alt: I2C wiring

  Fig.1: FT2232H i2c wiring. note the `FT_` prefix won't appear on the silkscreen of the `FT2232H-56Q` itself. The pullups on the bus are implemented as bodge jobs on channel board 9, soldered to the output of it's 3v3 regulator. In the future, powering them off the 3v3 rail from the `ft2232h-56q`  is most likely a better idea.

The sync pulse is also generated by the GPIO of the `ft2232h`, and is used by all boards to start a tx at the exact same time, and an rx at the exact same time. This extremely important to the operation of the phased array since any small delay introduced between the starts of tx/rx for different boards will mess up beamforming. The MCU clocks are not exactly the same, so we provide a sync pulse for both the start of the tx and the start of the rx, to "re-sync" the MCUs). The rising edge of the sync pulse controls a tx start, and the falling edge controls an rx start. We need to have a deterministic and price amount of time between the start of a tx and the start of an rx, since this delay has to be taken into account when range-finding. Furthermore, we want to be able vary the amount of time between the start of a tx and the start of an rx sequence, since having some delay between the end of the tx and the start of the rx allows the piezos to stop "ringing" before getting ready to receive the pulse. In practice, this just effects the minimum range that the phased array can image. the FT2232H cannot provide the deterministic timing for the sync pulse because it is controlled via USB by a non real time operating system (e.g. your computer), so the pulse width is non-deterministic. We solve this by using a 555 timer in a `monostable configuration`_, with a trim potentiometer to allow us to vary the pulse width. In practice, the stock room only has a 556 timer (basically two 555 timers in the same package), so we used this with some pins disconnected. See the wiring diagram:

.. _`monostable configuration`: https://www.electronics-tutorials.ws/waveforms/555_timer.html

.. figure:: figs/556_wiring.png
  :width: 400
  :alt: 556 wiring for sync pulse generation.

  Fig.2: 556 wiring for sync pulse generation. This was done on the breadboard next to channel 1.

The entire wiring schematic (and kicad project file) can be found at
``./figs/fish-n-chips-ft2232h``

fn generator
~~~~~~~~~~~~
We use a synced clock (bodge job) for the ADCs. Use a function generator for 1MHz square wave hooked up to the green clock distribution network. It should come in on extraio2.

Piezos
------
The wires for the piezos can be screwed into the central channel board by matching the number on the masking tape on the wire to the number on the label next to the channel board that the number corresponds to. These two digit numbers were meant to correspond to the row, col position of each piezo, but in reality, it's flipped. Note that the channel numbers on the central board do not correspond to any sort of channel location or i2c address, they are only internal to the switch board itself. In this documentation, boards are usually referred to by their i2c channel. Channel 1 is closest to the ft2232h chip, and the channels increase clockwise, until channel 9 at the end.
  
Note that to actually figure out where channel is given it's i2c address, see :py:attr:`i2c_cmd.PhasedArray.addrs`. (it's more clear to look directly at the `i2c_cmd.py` source file). Looking at the array from behind, this 2D array maps the piezo position to the i2c address of the board that controls it.

Make sure the tx/rx switch has the corresponding BNC wired to each channel board, and the channel board PAout is hooked up to the channelboard. Only one Channelboard's tx/rx switch needs to be hooked up to the AB input on the central board (we used channel 1).

Software
~~~~~~~~

Python
------

On the python side, you should be working in a `virtual environment`_. Verify you have an up-to-date python installation (I used python 3.9.6) and then, in a mac/linux shell in the ``scripts`` directory of the repository, run:

.. code-block:: console
		
   python -m venv venv_array
   source venv_array/bin/activate
   pip install -r requirements.txt

To create and activate the venv with all dependencies. Note that the commands in windows are slightly different, particularly the activation in the middle line. I believe running the ``activate.bat`` file in ``venv_array/bin/`` will suffice there.

Lastly, there is some additional setup for `pftdi` to install the proper USB drivers: `install instructions`_

.. _`virtual environment`: https://docs.python.org/3/tutorial/venv.html
.. _`install instructions`: https://eblot.github.io/pyftdi/installation.html#prerequisites

Sam4s development
-----------------

To program the channel boards themselves, we use `Microchip studio`_, which unfortunately only works on Windows. Over summer '21, we used an E79 laptop to run this.

Open the ``.atsln`` ("atmel solution", atmel being the name for the company that made the SAM4S before it got acquired) project file to get started.

We've tried to, for the most part, stick to using the `"Advanced Software Framework"`_ (ASF), which is a Hardware Abstraction Layer (HAL) that should, theoretically, ease development. In reality, while it does sometimes help to provide a board-agnostic layer, and is certainly helpful in some cases, it often causes trouble, and in reality, when bringing up (or modifying) peripherals, an in-depth understanding of the peripheral's user interface is usually needed. The `SAM4s datasheet`_ has good documentation of the SAM4s, and there exists a website do document ASF_ as well. In practice, it is also helpful to use the "go to definition" feature in Microchip Studio to open the ASF file where the function is implemented in the first place and get an idea of what is going on, since the ASF documentation is unclear.

Note that we bypass the ASF in the case of the ``PIOA`` interrupt handler, because the ASF-provided interrupt handler is super bloated. We replace the interrupt vector table (table containing all of the addresses to interrupt handlers) in order to bypass this. See comments in the ``src/main.c`` file itself for info. This file contains everything except for the clock configuration, which can be found in ``src/config/conf_clock.h``, and the crc calculation code taken from the internet (in public domain), which can be found in ``lib/crc.h``

To use a new peripheral for the first time, the specific module first needs to be loaded using the "ASF Wizard".

.. _`Microchip studio`: https://www.microchip.com/en-us/development-tools-tools-and-software/microchip-studio-for-avr-and-sam-devices#tabs
.. _`"Advanced Software Framework"`: https://asf.microchip.com/docs/latest/search.html?device=sam4s
.. _`SAM4s datasheet`: https://ww1.microchip.com/downloads/en/DeviceDoc/Atmel-11100-32-bit%20Cortex-M4-Microcontroller-SAM4S_Datasheet.pdf
.. _ASF: https://asf.microchip.com/docs/latest/search.html?device=sam4s

To actually program the sam4s, you need to use the Jlink programmer. Go `tools > device programming` to select the options for this. Make sure that everything is wired right and connected by reading the voltage of the bus, and it should be 3.3v. Then you can try reading the device ID.

The cable/connector used to connect to the MCU is often kind of sketchy, so don't freak out if it cannot connect. Try moving the connector around, or even pulling it out halfway, which often improves the connection.

Note that you need to set the specific flavor of SAM4s MCU that you are using before you can program it, because it checks the device ID. Most channel boards (1-7) have the ``SAM4S4B`` MCU, but the last two have ``SAM4SA16B`` MCUs since they were assembled during the chip-shortage following the pandemic when the other MCUs were no longer available. They are pin-compatible, follow the same datasheet, and the only real difference is memory/flash size and the existence of a special cache that we don't use.

Remember when programming all channel boards that you need to change the i2c address when you change the board you're programming!! An easy way to check that you didn't mess this up is try running ``python -i i2c_cmd.py`` and see if the instantiation of the PhasedArray object chokes up when addressing the channel boards to write DAC values.

Documentation
~~~~~~~~~~~~~

Building this doc uses sphinx. Ensure the python venv is activated, and, in the ``doc`` folder, run ``make clean; make html`` in a terminal to build. all files should appear in ``doc/build``.

The pip packages ``sphinx`` and ``sphinx_rtd_theme`` are required to build this documentation, as well as python packages required to import the documented modules: ``matplotlib``, ``numpy``, and ``pyftdi``.

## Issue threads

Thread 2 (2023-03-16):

### ISSUE TITLE
helpful !

### ISSUE THREAD

**Issue by 1kaiser** [HMC-ACE/muddUltrasound#2]
1. https://www.youtube.com/watch?v=vAEZvYlUnEM
2. https://www.youtube.com/watch?v=z4uxC7ISd-c
3. https://www.youtube.com/watch?v=Evao3XUUAOY
4. https://www.youtube.com/watch?v=h6321UBATps
5. https://www.youtube.com/watch?v=njDQKdZzGMI   <<< can his be used as replacement ?? if this is used in array or mesh mode

**Comment by AlecVercruysse** [comment]
Thank you for the resources! We haven't tested any other transducer element yet, but theoretically, other piezo transducers should work at well. Note that different elements have different resonant frequencies, however (for example, the JSN-SR04T-2.0 is resonant at 40kHz, but our current piezos are resonant at 92kHz). The transmit circuitry, MCU firmware, and beamforming source code would need to be modified to transition to elements of another frequency. Most likely, you'd want to change the spacing of the array as well.

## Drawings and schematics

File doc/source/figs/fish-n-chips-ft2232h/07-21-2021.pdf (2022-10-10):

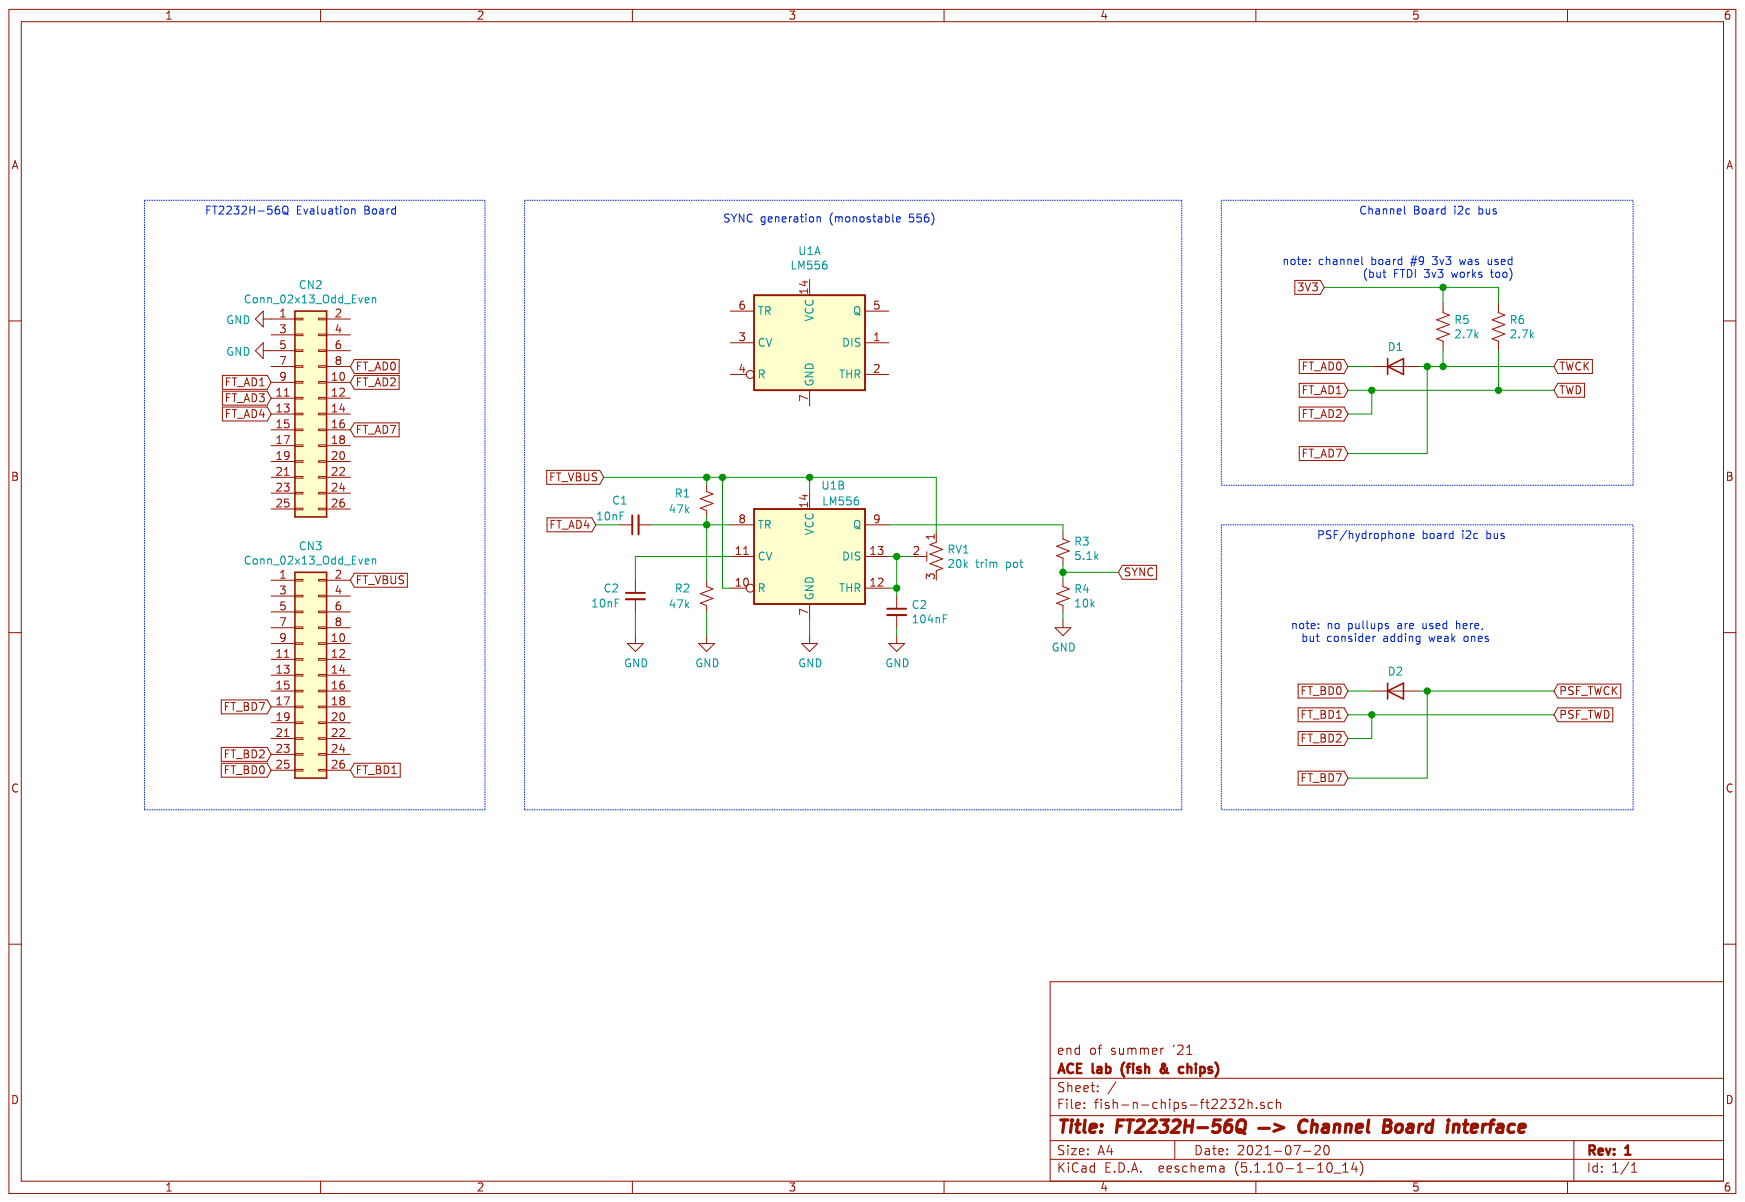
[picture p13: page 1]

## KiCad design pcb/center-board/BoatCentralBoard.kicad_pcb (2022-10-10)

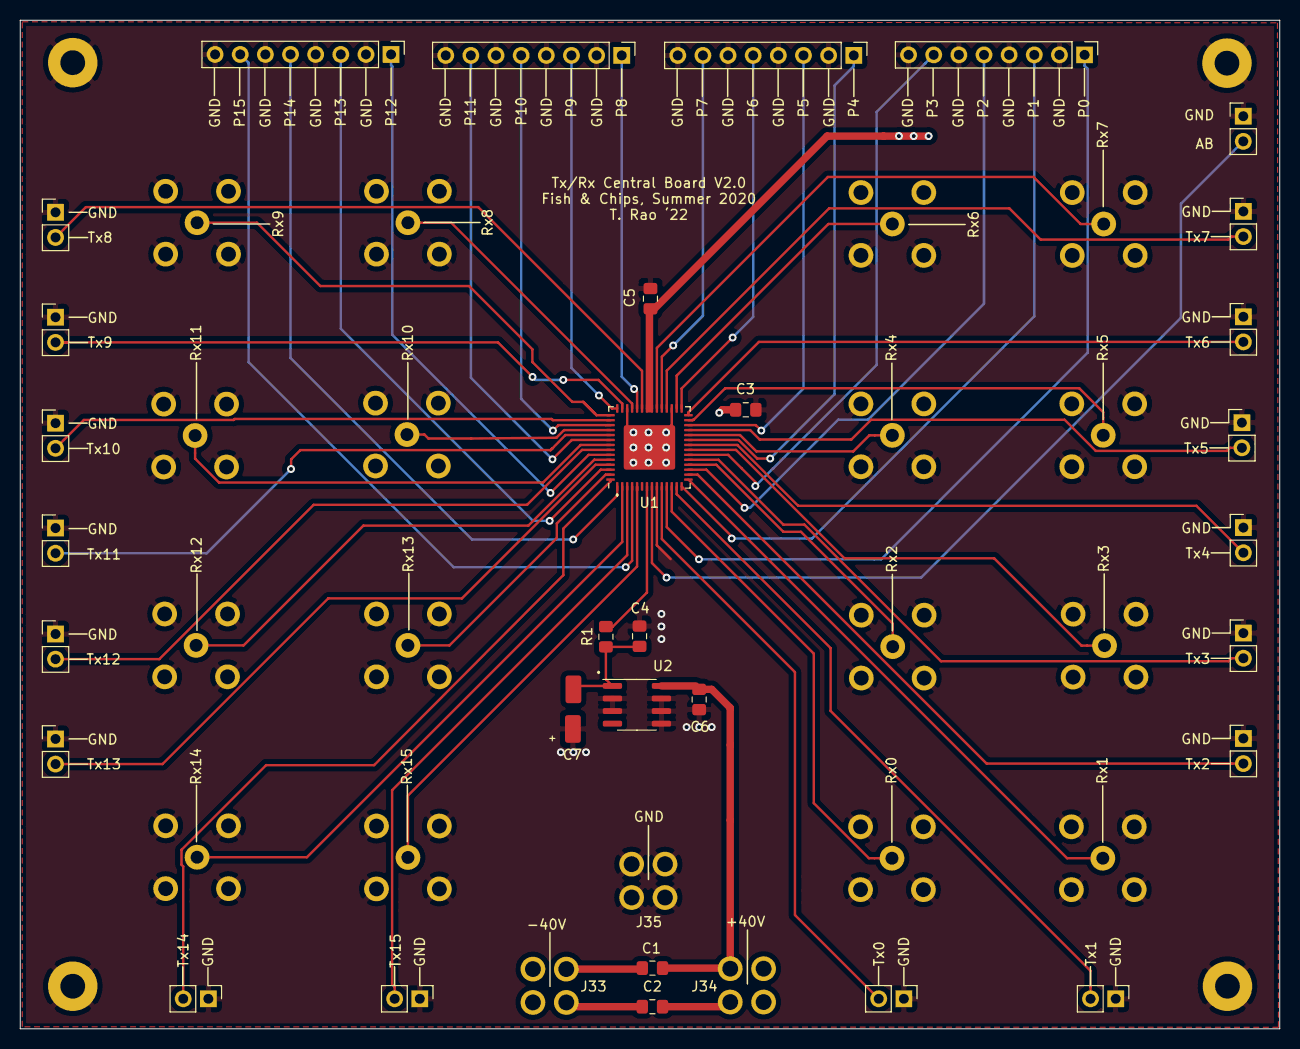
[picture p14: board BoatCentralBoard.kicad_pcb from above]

Board: 4 copper layers, 127.2 x 101.9 mm, 50 parts (0 on the bottom side), 54 nets.

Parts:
C1: 1μF; C_0805_2012Metric_Pad1.15x1.40mm_HandSolder
C2, C3, C4, C5: 0.1μF; C_0805_2012Metric_Pad1.15x1.40mm_HandSolder
C6: 0.1uF; C_0805_2012Metric_Pad1.15x1.40mm_HandSolder
C7: 47uF; 47uFBypass
J1, J3, J5, J7, J9, J11, J13, J15, J17, J19, J21, J23, J25, J27, J29, J31: Screw_Terminal_01x02; PinHeader_1x02_P2.54mm_Vertical
J2, J4, J6, J8, J10, J12, J14, J16, J18, J20, J22, J24, J26, J28, J30, J32: Conn_Coaxial; BNC_Vertical_Custom
J33, J34, J35: Conn_01x01; Banana_Jack_4Pin
J36, J37, J38, J39: Screw_Terminal_01x08; Pin_Header_Straight_1x08_Pitch2.54mm
J40: Screw_Terminal_01x02; Pin_Header_Straight_1x02_Pitch2.54mm
R1: 1k; R_0805_2012Metric_Pad1.15x1.40mm_HandSolder
U1: HV2808; QFN-56-1EP_8x8mm_P0.5mm_EP4.5x5.2mm
U2: LM2936HVBMAX-3.3; SOIC-8_3.9x4.9mm_P1.27mm

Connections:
0SW0: J1.2, U1.10
0SW1: J2.1, U1.12
0SW2: J3.2, U1.13
0SW3: J4.1, U1.15
0SW4: J5.2, U1.16
0SW5: J6.1, U1.18
0SW6: J7.2, U1.19
0SW7: J8.1, U1.21
0SW8: J9.2, U1.22
0SW9: J10.1, U1.24
0SW10: J11.2, U1.25
0SW11: J12.1, U1.27
0SW12: J13.2, U1.28
0SW13: J14.1, U1.30
0SW14: J15.2, U1.32
0SW15: J16.1, U1.34
0SW16: J17.2, U1.37
0SW17: J18.1, U1.39
0SW18: J19.2, U1.41
0SW19: J20.1, U1.43
0SW20: J21.2, U1.44
0SW21: J22.1, U1.46
0SW22: J23.2, U1.47
0SW23: J24.1, U1.49
0SW24: J25.2, U1.50
0SW25: J26.1, U1.52
0SW26: J27.2, U1.53
0SW27: J28.1, U1.55
0SW28: J29.2, U1.56
0SW29: J30.1, U1.2
0SW30: J31.2, U1.3
0SW31: J32.1, U1.5
0Y01: J36.1, U1.11
0Y23: J36.3, U1.14
0Y45: J36.5, U1.17
0Y67: J36.7, U1.20
0Y89: J37.1, U1.23
0Y1011: J37.3, U1.26
0Y1213: J37.5, U1.29
0Y1415: J37.7, U1.33
0Y1617: J38.1, U1.38
0Y1819: J38.3, U1.42
0Y2021: J38.5, U1.45
0Y2223: J38.7, U1.48
0Y2425: J39.1, U1.51
0Y2627: J39.3, U1.54
0Y2829: J39.5, U1.1
0Y3031: J39.7, U1.4
3.3: C4.1, C7.2, R1.2, U2.1
+40V: C1.1, C2.1, C5.1, C6.1, J34.1, U1.35, U1.36, U2.8
-40V: C1.2, C2.2, C3.1, J33.1, U1.31, U1.40, U1.57
AB: J40.2, U1.8
GND: C3.2, C4.2, C5.2, C6.2, C7.1, J1.1, J2.2, J3.1, J4.2, J5.1, J6.2, J7.1, J8.2, J9.1, J10.2, J11.1, J12.2, J13.1, J14.2, J15.1, J16.2, J17.1, J18.2, J19.1, J20.2, J21.1, J22.2, J23.1, J24.2, J25.1, J26.2, J27.1, J28.2, J29.1, J30.2, J31.1, J32.2, J35.1, J36.2, J36.4, J36.6, J36.8, J37.2, J37.4, J37.6, J37.8, J38.2, J38.4, J38.6, J38.8, J39.2, J39.4, J39.6, J39.8, J40.1, U1.9, U2.2, U2.3, U2.5, U2.6, U2.7
VDD: R1.1, U1.7

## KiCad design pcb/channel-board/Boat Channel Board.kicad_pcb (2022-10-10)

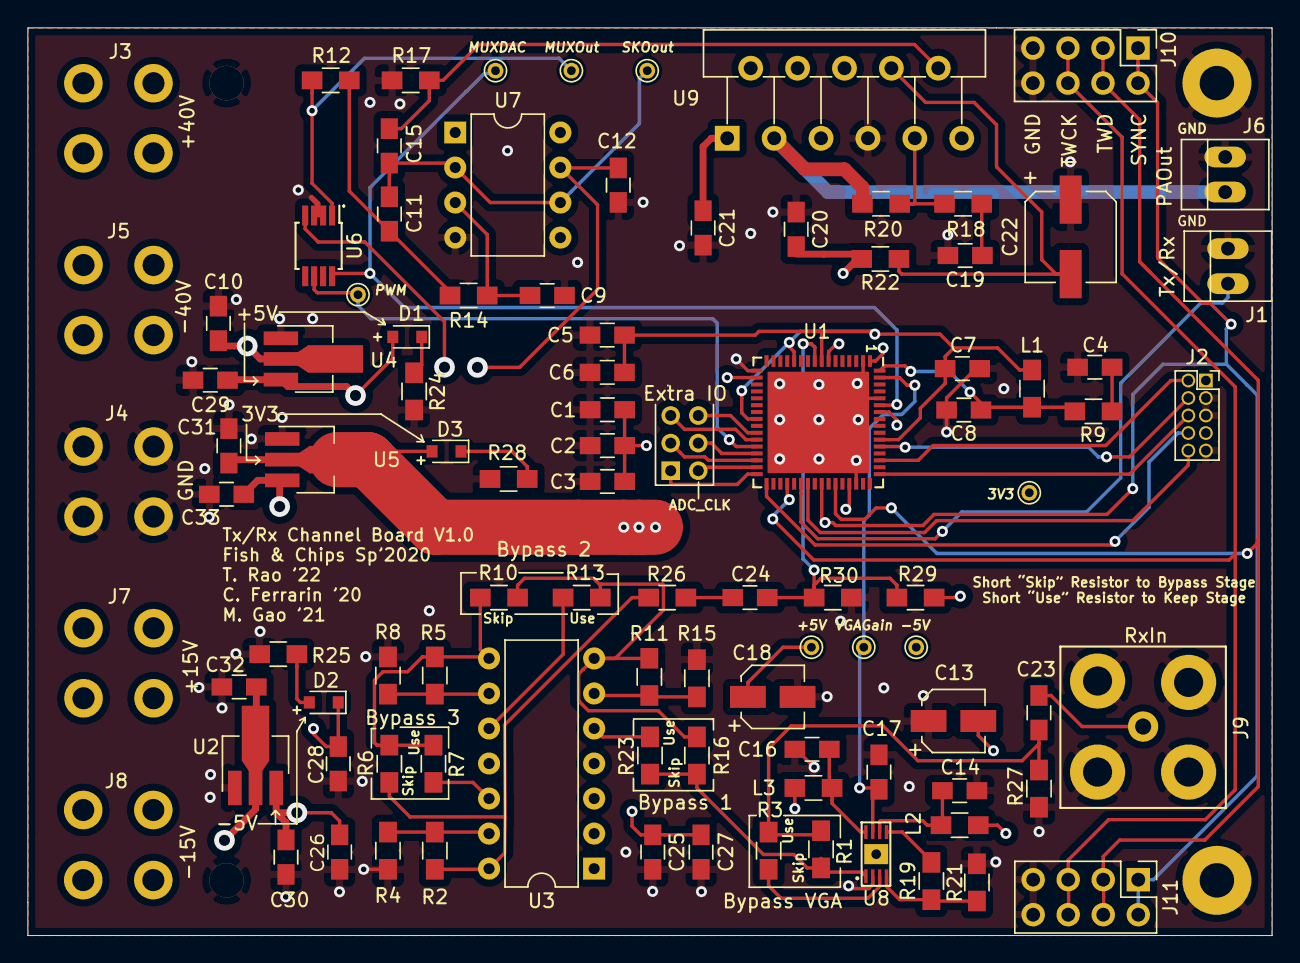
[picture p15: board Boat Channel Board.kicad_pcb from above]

Board: 4 copper layers, 90.2 x 65.8 mm, 98 parts (1 on the bottom side), 60 nets.

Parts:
3V3: PINTST
+5V: PINTST
-5V: PINTST
C1, C23: 10nF; C_0805_HandSoldering
C2, C3, C6, C7, C8, C25, C26: 100nF; C_0805_HandSoldering
C4: 4.7uF; C_0805_HandSoldering
C5: 2.2uF; C_0805_HandSoldering
C9: 10pF; C_0805_HandSoldering
C10, C33: 1uF; C_0805_HandSoldering
C11: 2.2nF; C_0805_HandSoldering
C12, C14, C16, C20, C21: 0.1µF; C_0805_HandSoldering
C13, C18: 10µF; CP_Elec_4x5.7
C15: 910pF; C_0805_HandSoldering
C17: 1nF; C_0805_HandSoldering
C19, C31: 22µF; C_0805_HandSoldering
C22: 100µF; CP_Elec_6.3x5.7
C24: 0.1μF; C_0805_HandSoldering
C27, C28, C30, C32: 0.1uF; C_0805_HandSoldering
C29: 10uF; C_0805_HandSoldering
D1, D2, D3: LED; D_0805
J1: TX/RX Switch; PINHEAD1-2
J2: Conn_02x05_Odd_Even; Socket_Strip_Straight_2x05_Pitch1.27mm
J3, J4, J5, J7, J8: Conn_01x01; Banana_Jack_4Pin
J6: Piezo; PINHEAD1-2
J9: Conn_Coaxial; BNC_Socket_TYCO-AMP_LargePads
J10, J11: Conn_02x04_Row_Letter_Last; Pin_Header_Straight_2x04_Pitch2.54mm
J12: Conn_01x06; Pin_Header_Straight_2x03_Pitch2.00mm
L1: 10uH; L_0805_HandSoldering
L2, L3: 120nH; L_0805_HandSoldering
MUXDAC: PINTST
MUXOut: PINTST
PWM: PINTST
R1, R3, R6, R7, R10, R13, R16, R23: 0Ω; R_0805_HandSoldering
R2, R5, R11, R17: 10kΩ; R_0805_HandSoldering
R4, R8, R15, R18, R27, R29, R30: 1kΩ; R_0805_HandSoldering
R9: 1; R_0805_HandSoldering
R12, R20: 20kΩ; R_0805_HandSoldering
R14: 6.98kΩ; R_0805_HandSoldering
R19, R21: 100Ω; R_0805_HandSoldering
R22: 15kΩ; R_0805_HandSoldering
R24, R25: 300Ω; R_0805_HandSoldering
R26: 1k; R_0805_HandSoldering
R28: 120Ω; R_0805_HandSoldering
SKOout: PINTST
U1: SAM4S4B; QFN-64-1EP_9x9mm_Pitch0.5mm
U2: L79L05_SOT89; SOT-89-3_Handsoldering
U3: TL084CP; DIP-14_W7.62mm
U4: ZXTR2005Z-13; SOT-89-3_Handsoldering
U5: AZ1117CH-3.3TRG1; SOT-89-3_Handsoldering
U6: MAX4644; MSOP-8_3x3mm_Pitch0.65mm
U7: MCP601-xP; DIP-8_W7.62mm
U8: AD8337; AD8337_LFCSP8_3x3
U9: LM3886T; TO-220-11_Vertical_StaggeredType1
VGAGain: PINTST

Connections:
3.3V: C1.2, C2.2, C3.2, C31.1, D3.2, J2.1, R29.1, U1.1, U1.7, U1.18, U1.45, U1.58, U5.2
+5V: +5V.1, C12.2, C18.1, C25.1, C27.2, C29.2, D1.2, L3.1, U3.4, U4.3, U6.4, U7.7
+15V: C10.2, C33.2, J7.1, U4.2, U5.3
+40V: C21.1, J3.1, U9.1, U9.5
-5V: -5V.1, C13.2, C26.1, C28.2, C30.2, D2.1, L2.1, U2.3, U3.11
-15V: C32.1, J8.1, U2.2
-40V: C20.2, J5.1, R22.2, U9.4
/IN+: C15.1, R17.1, U9.10
/PrAin+: R3.2, U8.3
/PrAin-: R19.1, R21.1, U8.4
/Vin+: C9.1, R14.1, U7.3
ADC_CLK: J12.2, U1.31
ADCin: C24.1, R29.2, R30.1, U1.9
ExtraIO1: J12.1, U1.32
ExtraIO3: J12.3, U1.30
ExtraIO4: J12.4, U1.29
ExtraIO5: J12.5, U1.27
ExtraIO6: J12.6, U1.26
GND: C1.1, C2.1, C3.1, C4.1, C5.1, C6.1, C7.1, C8.1, C9.2, C10.1, C12.1, C13.1, C14.2, C16.2, C17.1, C18.2, C19.2, C20.1, C21.2, C22.1, C25.2, C26.2, C27.1, C28.1, C29.1, C30.1, C31.2, C32.2, C33.1, J1.2, J2.3, J2.5, J2.9, J4.1, J6.2, J9.2, J10.7, J10.8, J11.7, J11.8, R4.1, R8.1, R15.1, R17.2, R21.2, R24.2, R25.2, R27.2, R28.2, R30.2, U1.2, U1.17, U1.46, U1.60, U1.65, U2.1, U4.1, U5.1, U6.2, U6.3, U7.4, U8.2, U9.7
GainIn: R1.2, R16.1, R23.1, U8.1
MUXOut: MUXOut.1, R12.2, U6.1
MUX_DAC: MUXDAC.1, U1.59, U6.8
unnamed: C4.2, R9.2
unnamed: C11.2, R12.1, R14.2
unnamed: C14.1, L2.2, U8.6
unnamed: C16.1, L3.2, U8.8
unnamed: C19.1, R18.2
unnamed: C22.2, R22.1, U9.8
unnamed: C23.1, J9.1
unnamed: C23.2, R1.1, R3.1, R27.1
unnamed: C24.2, R26.1
unnamed: D1.1, R24.1
unnamed: D2.2, R25.1
unnamed: D3.1, R28.1
unnamed: R2.1, R4.2, U3.13
unnamed: R2.2, R6.2, R26.2, U3.14
unnamed: R5.1, R8.2, U3.9
unnamed: R7.2, U3.12
unnamed: R10.1, R11.2, R13.1, R16.2, U3.7
unnamed: R5.2, R6.1, R7.1, R10.2, U3.8
unnamed: R11.1, R15.2, U3.6
unnamed: R13.2, U3.10
unnamed: R18.1, R20.2, U9.9
unnamed: R19.2, U8.5
unnamed: R23.2, U3.5
PAOut: J6.1, R20.1, U9.3
PWM: PWM.1, U1.28, U6.6
SAMNRST: J2.10, U1.39
SAMTCK: J2.4, U1.53
SAMTDI: J2.8, U1.33
SAMTDO: J2.6, U1.49
SAMTMS: J2.2, U1.51
SKOut: C11.1, C15.2, SKOout.1, U7.2, U7.6
SYNC: J10.1, J10.2, J11.1, J11.2, U1.41
TWCK: J10.5, J10.6, J11.5, J11.6, U1.36
TWD: J10.3, J10.4, J11.3, J11.4, U1.43
TXRX: J1.1, U1.38
VDDCORE: C5.2, C6.2, C7.2, L1.1, U1.8, U1.12, U1.24, U1.54
VDDPLL: C8.2, L1.2, R9.1, U1.64
VGAGain: C17.2, U1.63, U8.7, VGAGain.1

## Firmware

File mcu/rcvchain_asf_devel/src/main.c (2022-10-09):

/*
 * Alec Vercruysse 2021-03-20
 * avercruysse [at] hmc.edu
 * 
 * developed on ASF version 3.49.1
 * 
 * For Boat Channel Board v1.0. 
 * Rx: This code configures the ADC to trigger off the TC0 and send
 * <FRAME_SIZE> number of samples to the <frame_buffer> via the Peripheral DMA Controller (pdc).
 * It also configures a TWI interface on <TWI_ADDR> with a basic api, mainly to read values from frame_buffer.
 *
 * See twi_config() for information on how to communicate over TWI with the bus pirate. Note that the address
 * of this is a 7-bit i2c addr. So when addressing via the bus pirate, you need to use `(TWI_ADDR << 1) | READ`,
 * where READ is a bit specifying whether you are reading from the mcu or not.
 * 
 * The ADC should sample at approximately 1 MHz (hard to confirm, but it's configured for exactly 1MHz), and >.989 MHz.
 * 108kB (54*1024=55296 samples) corresponds to 55.296 ms of capture time @1Mhz. At V_sound = 1482 m/s underwater, using
 * 
 *	Distance [m] = 1482 [m/s] * 55.296 [ms] * 0.001 [s/ms] * 0.5 [round-trip factor]	
 *               = 40.97 m
 *
 * To test the receiver, the i2c interface also allows for the output sine wave to be turned off/on. This uses the dac
 * and the PWM peripherals.
 * 
 */

#include <asf.h>
#include "main.h"
#include <math.h>
#include "lib/crc.h"

#define TWI_ADDR  1

/** pin defs **/
#define TX_RX_SWITCH PIO_PA28
#define SYNC_PIN     PIO_PA29
#define SYNC_PIN_IDX PIO_PA29_IDX
#define EXTRAIO_1    PIO_PA7
#define EXTRAIO_2    PIO_PA8
#define EXTRAIO_3    PIO_PA9
#define EXTRAIO_4    PIO_PA10
#define EXTRAIO_5    PIO_PA12
#define EXTRAIO_6    PIO_PA26

/** DAC/PWM parameters **/
#define PWM_FREQ 92000          // aim for 92KHz sine
#define PWM_PERIOD 130          // clka freq [hz] = period [counts] * pwm freq [Hz].
#define PWM_DUTY_CYCLE 65       // half of period
volatile uint32_t muxdac = 837; // initial DAC value for MUX_DAX, ~1V
volatile uint32_t vgadac = 0;   // initial DAC value for VGAgain 
volatile uint32_t phase = 0;    // initial phase delay (in ns)

/** delay/burst parameters **/
#define BURST_DURATION 100               // us
volatile uint64_t phase_cycle_count = 1; // can't be zero!

/** ADC capture parameters **/
#define KB 1024
#define FRAME_SIZE 20 * KB // 40 kB (2 bytes/uint16_t) ~20kb left for all other stuff. sets PDC RCR register (number of samples to take).
#define MSG_LEN 1024       // how many bytes sent before each checksum

uint16_t frame_buffer[FRAME_SIZE];
pdc_packet_t adc_packet; // will point to frame_buffer

/* program status booleans */
volatile uint8_t capture_complete = 0; // set to one when capture is complete
volatile uint8_t setup_complete = 0; 
volatile uint8_t status_receiving_bufferidx = 0; // waiting for second byte from master to set bufferidx. first byte in cmd is 0x1. for debugging (can only do 0-255).
volatile uint8_t status_receiving_muxdac = 0; // set if waiting for set byte to set channel 0 of dacc (MUXDAC).
volatile uint8_t status_receiving_vgadac = 0; // set if waiting for set byte to set channel 1 of dacc (VGAgain).
volatile uint8_t status_receiving_phase = 0;  // set if waiting for value of phase 
volatile uint8_t byte_transfer_idx = 0;       // if receiving muxdac or vgadac value, the index of the byte. 
volatile uint8_t write_mode = 0; // THR only filled when this is 1. automatically reset at NACK (end of I2C transmission). set with a write to 0x00.

/************************************************************************/
/* NVIC -- CUSTOM VECTOR INTERRUPT TABLE IN RAM                         */
/************************************************************************/
/* This is required since we use the HAL. ASF takes over the PIOA_Handler()
 * function that the interrupt table normally points to (in `pio_handler.c`)
 * but that handler function is not deterministic and super slow (~12us).
 * we replace the vector interrupt for PIOA with our own, and ensure the only
 * interrupt triggering PIOA is the sync handler. See the CMSIS `NVIC_SetVector`
 * fn doc for details. (we need to move the entire table from ROM to RAM)
 */
#define VECTORTABLE_SIZE (240)         // probably an overestimate, but no harm I think.
#define VECTORTABLE_ALIGNMENT (0x100U) // 16 cortex + 32 external interrupts = 48 words. next power of 2 = 256
uint32_t vectorTable_RAM[VECTORTABLE_SIZE] __attribute__((aligned (VECTORTABLE_ALIGNMENT)));

void replace_interrupt_table(void) {
	uint32_t i;
	uint32_t *vectors = (uint32_t *)SCB->VTOR;
	for (i = 0; i < VECTORTABLE_SIZE; i++) {
		vectorTable_RAM[i] = vectors[i];
	}

	// relocate vector table
	__disable_irq();
	SCB->VTOR = (uint32_t) &vectorTable_RAM;
	__DSB();
	__enable_irq();
}

/************************************************************************/
/* END NVIC                                                             */
/************************************************************************/

/* 
 * Initialize the twi0 interface as peripheral.
 */
void twi_init(void) {
	twi_slave_setup(TWI0, TWI_ADDR); // address needs to be set first!
		
	pio_pull_up(PIOA, PIO_PA3A_TWD0, 0); // disable pullup
	pio_pull_up(PIOA, PIO_PA4A_TWCK0, 0);

	//disable PIO control of pins to enable peripheral control
	REG_PIOA_PDR |= PIO_PDR_P3;
	REG_PIOA_PDR |= PIO_PDR_P4;
	
	/* Clear receipt buffer */
	twi_read_byte(TWI0);

	/* Configure TWI interrupts */
	NVIC_DisableIRQ(TWI0_IRQn);
	NVIC_ClearPendingIRQ(TWI0_IRQn);
	NVIC_SetPriority(TWI0_IRQn, 0);
	NVIC_EnableIRQ(TWI0_IRQn);
	twi_enable_interrupt(TWI0, TWI_SR_SVACC);
}

/*
 * Initializes PA28 (TX/RX A/B Signal) for basic logic output.
 * requires pio to have it's clock first! done in main.
 */
void tx_rx_switch_init() {
	pio_set_output(PIOA, TX_RX_SWITCH, LOW, DISABLE, DISABLE);
	tx_mode(); // default
}

void tx_mode() {
	pio_set(PIOA, TX_RX_SWITCH);
}

void rx_mode() {
	pio_clear(PIOA, TX_RX_SWITCH);
}

// for setting gpio pins in order to debug. must be called after twi_init
void extraio_init(void) {
	pio_set_output(PIOA, EXTRAIO_1, LOW, DISABLE, ENABLE); // see sam pio quickstart ASF doc.
	// pio_set_output(PIOA, EXTRAIO_2, LOW, DISABLE, ENABLE); // EXTRAIO2 is used by ADC as external trigger 2021-06-14.
	pio_set_output(PIOA, EXTRAIO_3, LOW, DISABLE, ENABLE);
	pio_set_output(PIOA, EXTRAIO_4, LOW, DISABLE, ENABLE);
	pio_set_output(PIOA, EXTRAIO_5, LOW, DISABLE, ENABLE);
	pio_set_output(PIOA, EXTRAIO_6, LOW, DISABLE, ENABLE);

	pio_clear(PIOA, EXTRAIO_1);
	pio_clear(PIOA, EXTRAIO_3);
	pio_clear(PIOA, EXTRAIO_4);
	pio_clear(PIOA, EXTRAIO_5);
	pio_clear(PIOA, EXTRAIO_6);
}


/*
 * Sync pin change interrupt handler. Performs the pulse.
 * DON'T SET ANY OTHER INTERRUPTS ON PIOA!
 * controls the logic of a tx/rx sequence.
 */
void PIOA_Handler_override(void) {
	uint32_t status = pio_get_interrupt_status(PIOA); // read to clear
	uint8_t  sync_level = pio_get(PIOA, PIO_TYPE_PIO_INPUT, SYNC_PIN);
	if (sync_level) { // when sync goes high, start pulse
		portable_delay_cycles(phase_cycle_count);
		start_pwm();
		delay_us(BURST_DURATION);
		stop_pwm();
	} else {         // when sync goes low, start capture
		restart_capture();
	}
}

void sync_handler_unused(uint32_t a, uint32_t b) {} // unused (see below)
void sync_init() {
	uint32_t sync_attrs = PIO_DEGLITCH;
	pio_set_input(PIOA, SYNC_PIN, sync_attrs);
		
	NVIC_ClearPendingIRQ(PIOA_IRQn);
	NVIC_SetPriority(PIOA_IRQn, 0);
	NVIC_SetVector(PIOA_IRQn, (uint32_t) PIOA_Handler_override);
	NVIC_EnableIRQ(PIOA_IRQn);

	// we use this function to set the trigger attributes we want in registers
	// but we override the ASF handler, so sync_handler_unused is never called
	pio_handler_set_pin(SYNC_PIN_IDX, PIO_DEFAULT, sync_handler_unused); // by default, edge detection interru
	pio_enable_interrupt(PIOA, SYNC_PIN);
}

/* 
 * Resets PDC and re-enables the DAC capture. Assumes everything has already been initialized!
 * (ADC, TC0, P DMA, all clocks). This is just a reset!
 */
void restart_capture() {
		Pdc* adc_pdc = adc_get_pdc_base(ADC);
		adc_packet.ul_addr = (uint32_t) frame_buffer;
		adc_packet.ul_size = FRAME_SIZE;
		pdc_rx_init(adc_pdc, &adc_packet, NULL); // initialize pdc to point to frame_buffer. No next packet.
		pdc_enable_transfer(adc_pdc, PERIPH_PTCR_RXTEN); // receive transfer enable.
		
		rx_mode();
		adc_enable_channel(ADC, ADC_CHANNEL_0);
}
volatile uint32_t bufferidx = 0;
volatile uint8_t error = 0; // holds |= SCLWS  to see if clock synchronization or clock stretching is occurring.
	

/* cycles are like 14 cpu cycles-ish. it's confusing.
 */
uint64_t ns_to_cy(volatile uint32_t ns) {
		uint32_t f_cpu = sysclk_get_cpu_hz();
		volatile uint64_t cy = (uint64_t) round((( (double) ns / 1000 ) * (f_cpu) + (14e6 - 1ul)) / 14e6);
		return cy; // offset all delays by 1 (since we can't have a delay of 0)
}


// returns status (1 if not done with rcv)
uint8_t byte_transfer(uint8_t read, volatile uint32_t* dest) {
	if (byte_transfer_idx == 0) *dest = 0; // reset on first byte
	*dest |= read << (8*byte_transfer_idx++); // LSB first
	if (byte_transfer_idx == 4) { // range 0-3 for 32 bit int.
		byte_transfer_idx = 0;
		return 0; // done with transfer	
	}
	return 1; // not done with transfer
}

uint8_t crc_sent = TRUE;
uint32_t current_crc = 0;

void fill_i2c_thr() {
	static uint8_t crc_byte_idx = 0;
	
	if (bufferidx == FRAME_SIZE*2 && crc_sent) {                  // overflow!
		REG_TWI0_THR = 0; 
	} else if (bufferidx > 1 && !(bufferidx % MSG_LEN) && !crc_sent) { // if we're at a multiple of MSG_LEN
		if (!crc_byte_idx) {
			unsigned char const* ptr = ((uint8_t*) frame_buffer) + bufferidx - MSG_LEN;
			current_crc = (uint32_t) crcFast(ptr, MSG_LEN);
		}
		uint8_t tmp = ((uint8_t*) &current_crc)[crc_byte_idx++];
		REG_TWI0_THR = tmp;
		if (crc_byte_idx == 4) {
			crc_byte_idx = 0;
			crc_sent = TRUE;
		}
} else {
		// increment by byte in a 16-bit array.
		// NOTE: LSB COMES FIRST, THEN MSB!! see https://onlinegdb.com/WXNtuq3jd7
		REG_TWI0_THR = *(((uint8_t*) frame_buffer) + bufferidx++);
		crc_sent = FALSE;
	}
}

/*
 * TODO: refactor this for ASF use.
 * https://ww1.microchip.com/downloads/en/AppNotes/Atmel-42273-SAM4-TWI-Slave-Mode-Driver_ApplicationNote_AT07335.pdf
 */
void TWI0_Handler(void) {
	uint32_t status = REG_TWI0_SR;

	if (status & TWI_SR_SVREAD) { // master read operation (mcu writes)
		if ((status & TWI_SR_TXRDY)) { 
			pio_set(PIOA, EXTRAIO_6); // fill THR
			fill_i2c_thr();
		}
	} else {                      // master write operation (mcu reads)
		if (status & TWI_SR_RXRDY) {
				uint8_t read_byte = REG_TWI0_RHR;
				if (status_receiving_bufferidx) {
					status_receiving_bufferidx = 0;
					bufferidx = read_byte;
				} else if (status_receiving_muxdac) {
					status_receiving_muxdac = byte_transfer(read_byte, &muxdac);
					if (!status_receiving_muxdac) dacc_write_channel(0, muxdac);
				} else if (status_receiving_vgadac) {
					status_receiving_vgadac = byte_transfer(read_byte, &vgadac);
					if (!status_receiving_vgadac) // if rcv ended
						dacc_write_channel(1, vgadac);
			    } else if (status_receiving_phase) {
					status_receiving_phase = byte_transfer(read_byte, &phase);
					if (!status_receiving_phase) // if rcv ended
						phase_cycle_count = ns_to_cy(phase);
				} else {
				switch(read_byte) {
					case 42: tx_mode();
					break;
					case 43: rx_mode();
					break;
					case 00: { 
						bufferidx = 0; 
						crc_sent = TRUE;
					}
					break;
					case 01: status_receiving_bufferidx = 1; break;
					case 02: restart_capture(); break;
					case 03: start_pwm(); break;
					case 04: stop_pwm(); break;
					case 05: status_receiving_muxdac = 1; break;
					case 06: status_receiving_vgadac = 1; break;
					case 102: status_receiving_phase = 1;  break;
				}
			}
		}
	}
}
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
